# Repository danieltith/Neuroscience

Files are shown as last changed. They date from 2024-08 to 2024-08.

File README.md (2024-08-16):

# Neuroscience

Code and hardware files related to my PhD thesis: "Mapping associations between early life adversity and alcohol use disorder through human epidemiology and rat neurobiology".

[Link to be inserted once publicly available]

References:

Brown LA, Hasan S, Foster RG and Peirson SN. COMPASS: Continuous Open Mouse Phenotyping of Activity and Sleep Status [version 2; peer review: 4 approved]. Wellcome Open Res (2017) 1:2. (https://doi.org/10.12688/wellcomeopenres.9892.2)

Akam T, Lustig A, Rowland JM, Kapanaiah SKT, Esteve-Agraz J, Panniello M, Márquez C, Kohl MM, Kätzel D, Costa RM, Walton ME. Open-source, Python-based, hardware and software for controlling behavioural neuroscience experiments. eLife (2022) 11:e67846. (https://doi.org/10.7554/eLife.67846)

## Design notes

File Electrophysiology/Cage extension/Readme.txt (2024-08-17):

Box extension made of 5mm clear acrylic.
Corners strengthened using 10x10mm acrylic bar.
Contains space to house operant unit or blanking plate during recording. 
N.B if working with female rats would recommend extending height to 30+cm due to climbing.

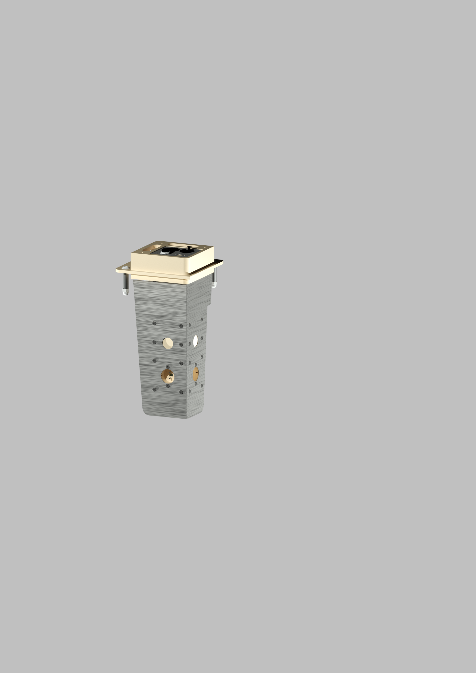
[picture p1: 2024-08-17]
Operant/OperantUnit/Render2.png

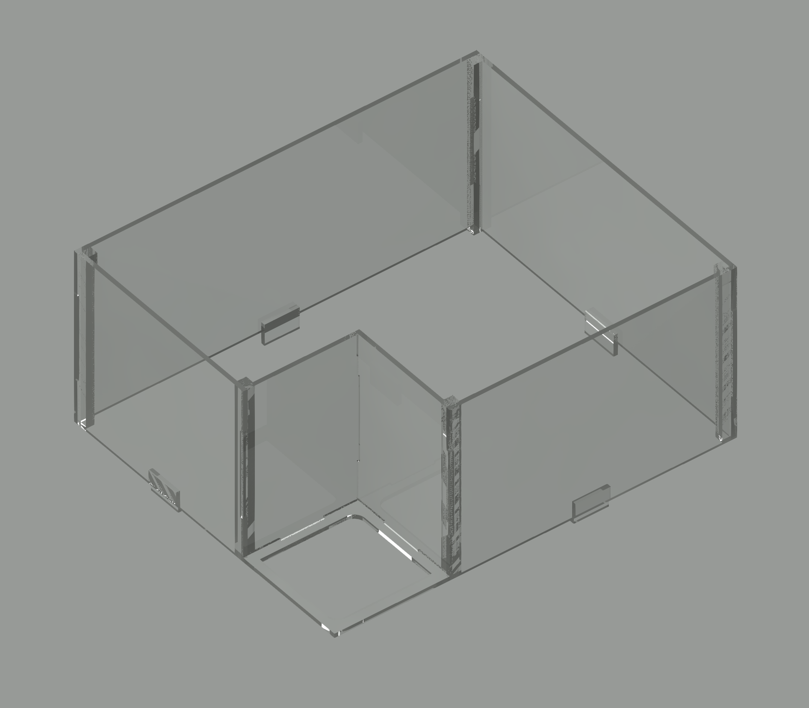
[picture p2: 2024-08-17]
Electrophysiology/Cage extension/Render.png

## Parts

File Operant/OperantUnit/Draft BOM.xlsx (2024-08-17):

Part Name/description | Supplier | Supplier PN | Quantity | Package size | Approx Price per unit | Approx Total
Stainless Steel Pipes/Thin-Walled, 2mm OD, 1mm ID, annealled | Misumi | SPLT2-28 | 2 | 1 | 2.93 € | 5.86 €
TRX Slim Head Screw M3 - 8mm | Misumi | CSXSLH-STN-M3-8 (https://uk.misumi-ec.com/vona2/detail/221005017402/?HissuCode=CSXSLH-STN-M3-8) | 1 | 2000 | 82.44 € | 82.44 €
TRX Slim Head Screw M3 - 16mm | Misumi | CSXSLH-STN-M3-16 (https://uk.misumi-ec.com/vona2/detail/221005017402/?HissuCode=CSXSLH-STN-M3-16) | 1 | 1000 | 54.83 € | 54.83 €
TRX Slim Head Screw M3 - 25mm | Misumi | CSXSLH-STN-M3-25 (https://uk.misumi-ec.com/vona2/detail/221005017402/?HissuCode=CSXSLH-STN-M3-25) | 1 | 500 | 38.14 € | 38.14 €
TRX Slim Head Screw M3 - 30mm | Misumi | CSXSLH-STN-M3-30 (https://uk.misumi-ec.com/vona2/detail/221005017402/?HissuCode=CSXSLH-STN-M3-30) | 1 | 500 | 41.67 € | 41.67 €
10uL fixed volume pump | Lee Company | LPMA1250110L | 2 | 1 | £173.95 | £347.90
Quiet 3 port HDI Solenoid valve | Lee Company | LHQA1231220H | 2 | 1 | £64.11 | £128.22
Stainless steel panels | Cut-Tec | NA | 1 | 1 set
Nosepoke PCBs | Newbury Electronics | NA | 2 | 1
Breakout PCB | Newbury Electronics | NA | 1 | 1
Indicator light PCBs | Newbury Electronics |  | 2 | 1
Pyboard D | Micropython
Molex picoblade cable assemblies | Digikey

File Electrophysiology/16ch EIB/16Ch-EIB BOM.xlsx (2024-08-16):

Description | Quantity | Manufacturer | Manufacturer Part Number | Supplier | Supplier Part Number | Designator | Technology
DF40C(2.0)-70DS-0.4V(51) | 1 | Hirose Connector (https://www.mouser.co.uk/manufacturer/hirose/) | DF40C(2.0)-70DS-0.4V(51) | Mouser | 798-DF40C2070DS04V51 | J1 | SMD
WA-SMSI M1.6 x 2.5mm D3.3mm | 1 | Wurth Elektronik | 97730256330R | Mouser | 710-97730256330R | MP1 | SMD

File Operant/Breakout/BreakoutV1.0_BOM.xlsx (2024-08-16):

Part Number | Designator | Description | Mount | Required Quantitiy | Manufacturer | Manufacturer PN | Supplier | Supplier PN
1 | C1 | Ceramic Capacitor 100V 100nF 0805 | SMD | 1 | KEMET | C0805C104K1RAC7210 | Digikey | 399-C0805C104K1RAC7210CT-ND
2 | C2,C3,C4 | Capacitor 16V 1uF 0603 | SMD | 3 |  |  | Newbury free stock | 0603-1uF-16V
3 | C5,C6,C7,C8 | Capacitor 25V 10uF 1206 | SMD | 4 |  |  | Newbury free stock | 1206-10uf-25V
4 | D1 | Diode Schottky 20V 1A | SMD | 1 | Toshiba | CRS06(TE85L,Q,M) | Digikey | CRS06QMCT-ND
5 | D2 | Diode Schottky 10V 3A | SMD | 1 | Infineon | BAT60AE6327HTSA1 | Digikey | BAT60AE6327HTSA1CT-ND
6 | D3,D4,D5,D6 | Diode TVS 24V 0603 | SMD | 4 | Littelfuse | PGB1010603MR | Digikey | F3801CT-ND
7 | IC1,IC2,IC3 | Driver Array | SMD | 3 | Toshiba | TBD62083AFWG | Digikey | TBD62083AFWGELCT-ND
8 | IC4 | USB TYPE-C PD CTRL, -40 TO 105DEG C | QFN | 1 | STMICROELECTRONICS | STUSB4500QTR | Digikey | 497-18060-1-ND
9 | J1 | USB-C connector | THT | 1 | Amphenol ICC (Commercial Products) | MUSBRM1C130 | Digikey | MUSBRM1C130-ND
10 | J2,J3,J4 | 4 pin through hole connector | THT | 3 | Molex | 530470410 | Digikey | WM1733-ND
11 | J5,J6,J7,J8,J9,J10,J11,J12,J13,J14,J15,J16,J17,J18,J19,J20 | 2 pin through hole connector | THT | 16 | Molex | 530470210 | Digikey | WM1731-ND
12 | J21,J22,J23 | 5 pin through hole connector | THT | 3 | Molex | 530470510 | Digikey | WM1734-ND
13 | Q1 | Power MOSFET | SMD | 1 | STMICROELECTRONICS | STL9P3LLH6 | Digikey | 497-17897-1-ND
14 | R1,R2,R3,R4,R5,R6 | 100 resistor; 0603; 0.1W | SMD | 6 |  |  | Newbury free stock | 0603-100R
15 | R7,R8 | 1k resistor; 0603; 0.1W | SMD | 2 |  |  | Newbury free stock | 0603-1K
16 | R9,R10,R11,R12 | 2.2k resistor; 0603; 0.1W | SMD | 4 |  |  | Newbury free stock | 0603-2K2
17 | R13 | 22k resistor; 0603; 0.1W | SMD | 1 |  |  | Newbury free stock | 0603-22K
18 | R14,R15,R16,R17,R18 | 100k resistor; 0603; 0.1W | SMD | 5 |  |  | Newbury free stock | 0603-100K
19 | S1,S2,S3 | SPST push switch | SMD | 3 | OMRON | B3FS-1012P | Digikey | SW1440CT-ND
20 | U1 | 5V 1A DC DC Converter | THT | 1 | Recom Power | R-78E5.0-1.0 | Digikey | 945-2201-ND
21 | U2 | 12V 1A DC DC Converter | THT | 1 | Recom Power | R-78E12-1.0/X9 | Digikey | 945-R-78E12-1.0/X9-ND
22 | X1,X2 | WBUS40 connector | SMD | 2 | Hirose Electric Co Ltd | DF40HC(4.0)-40DS-0.4V(70) | Digikey | H124604CT-ND

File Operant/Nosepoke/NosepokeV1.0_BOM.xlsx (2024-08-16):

Part Number | Designator | Description | Mount | Quantity | Manufacturer | Manufacturer PN | Supplier | Supplier PN
1 | C1,C2 | 10 uF Capacitor 0603 | SMD | 2 |  |  | Newbury free stock | 0603-10uF-6.3V
2 | C3 | 100nF Capacitor 0603 | SMD | 1 |  |  | Newbury free stock | 0603-100nF-25V
3 | J1,J2 | Right angle header | THT | 2 | SAMTEC | SSW-102-02-T-S-RA | Digikey | SAM11929-ND
4 | J3,J4,J5,J6,J7 | 2 pin connector | THT | 5 | Molex | 530470210 | Digikey | 455-1611-ND
5 | J8 | 5 pin connector | THT | 1 | Molex | 530470510 | Digikey | WM1734-ND
6 | Q1,Q2 | Mosfet | SMD | 2 |  | BSS138 | Farnell | 9845330
7 | R1 | 220R resistor 0603 | SMD | 1 |  |  | Newbury free stock | 0603-220R
8 | R2,R3,R4,R5,R6 | 10k resistor 0603 | SMD | 5 |  |  | Newbury free stock | 0603-10k
9 | R7,R8 | 47k resistor 0603 | SMD | 2 |  |  | Newbury free stock | 0603-47K
10 | U1 | TOF sensor | Leadless | 1 | ST Microelectronics | VL6180XV0NR/1 | Digikey | 497-14702-1-ND
11 | U2 | LP5907 2.8V LDO | SMD | 1 | TEXAS INSTRUMENTS | LP5907MFX-2.8/NOPB | Farnell | 3007717

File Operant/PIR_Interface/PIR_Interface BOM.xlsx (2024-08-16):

Description | Quantity | Manufacturer | Manufacturer Part Number | Supplier | Supplier Part Number | Designator | Technology
Arduino Nano v.3.x (ATmega328) | 1 | Arduino | A000005 | Digikey | 1050-1001-ND | A1 | THT
12 port ethernet connector | 1 | Stewart Connector | SS73100-046F | Digikey | 380-1225-ND | J1 | THT

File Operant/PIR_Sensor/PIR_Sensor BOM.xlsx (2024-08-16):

Description | Quantity | Manufacturer | Manufacturer Part Number | Supplier | Supplier Part Number | Designator | Technology
RJ45 jack | 1 | AMPHENOL | 54601-908WPLF | Digikey | 609-5081-ND | J1 | THT
8 pin header (2.54mm) | 1 | Wurth Electronic | 61300811821 | Digikey | 732-61300811821-ND | J2 | THT
5V PIR sensor (AMN32111) | 1 | Panasonic | AMN32111 | Digikey | 255-2645-ND | U1 | THT
SMD resistor (6K2; 1%; 0.25W; 1206) | 2 | STACKPOLE ELECTRONICS INC (VA) | RMCF1206FT6K20 | Digikey | RMCF1206FT6K20CT-ND | R1, R5, | SMD
SMD resistor (10K; 1%; 0.5W; 1206) | 2 | STACKPOLE ELECTRONICS INC (VA) | RNCP1206FTD10K0 | Digikey | RNCP1206FTD10K0CT-ND | R2, R4 | SMD
Light Dependent Resistor | 1 |  |  |  |  | R3 | THT
Black ABS Potting Box Enclosure with Lid - 39.5x27.5x17.5mm - | 1 | Evatron | RX2006 | Farnell | EN84693 | NA | NA

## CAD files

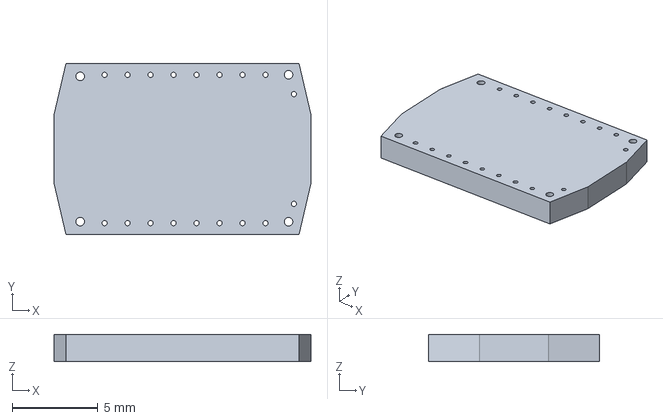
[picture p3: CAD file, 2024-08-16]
Electrophysiology/16ch EIB/KiCAD project/eob-16.step
15.0 x 10.0 x 1.60 mm

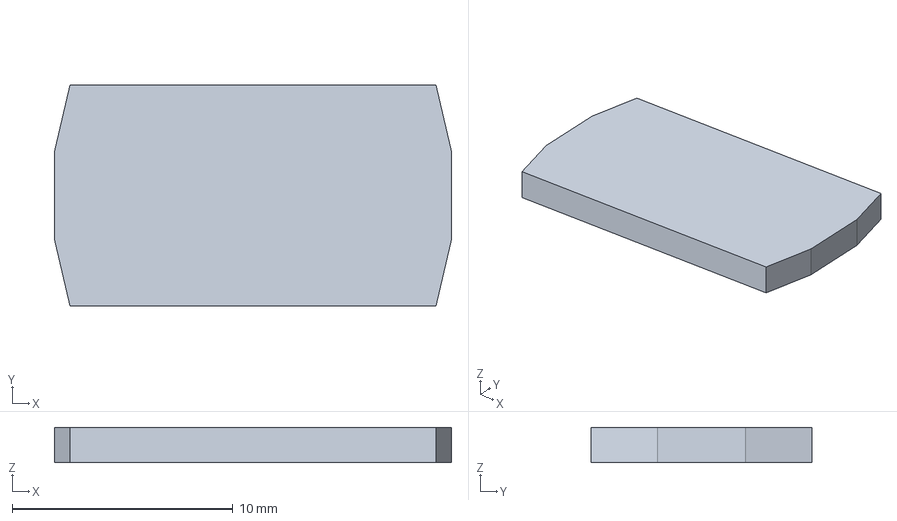
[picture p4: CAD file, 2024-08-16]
Electrophysiology/Head cap for 16ch EIB/KiCAD/12X18_CAP.step
18.0 x 10.0 x 1.60 mm

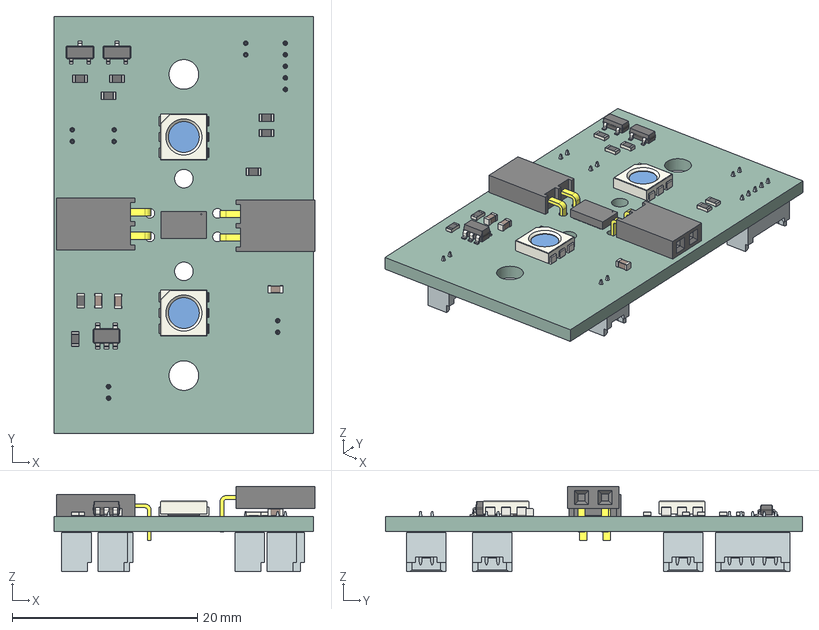
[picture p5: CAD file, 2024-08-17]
Operant/Nosepoke/KiCadFiles/NosepokeV1.0.step
28.1 x 45.0 x 9.21 mm
C_0603_1608Metric x 3
SOT_23 x 2
R_0603_1608Metric x 8
ssw-102-02-t-s-ra x 2
LED_RGB_5050_6 x 2
SOT_23_5
530470210wbm000_01 x 5
530470510wbm000_01
_autosave-NosepokeV1.0_PCB

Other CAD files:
Electrophysiology/Cage extension/FinalCageExtension.dwg

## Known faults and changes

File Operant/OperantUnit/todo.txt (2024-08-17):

1) Update BOM
2) Include laser cutting sheets

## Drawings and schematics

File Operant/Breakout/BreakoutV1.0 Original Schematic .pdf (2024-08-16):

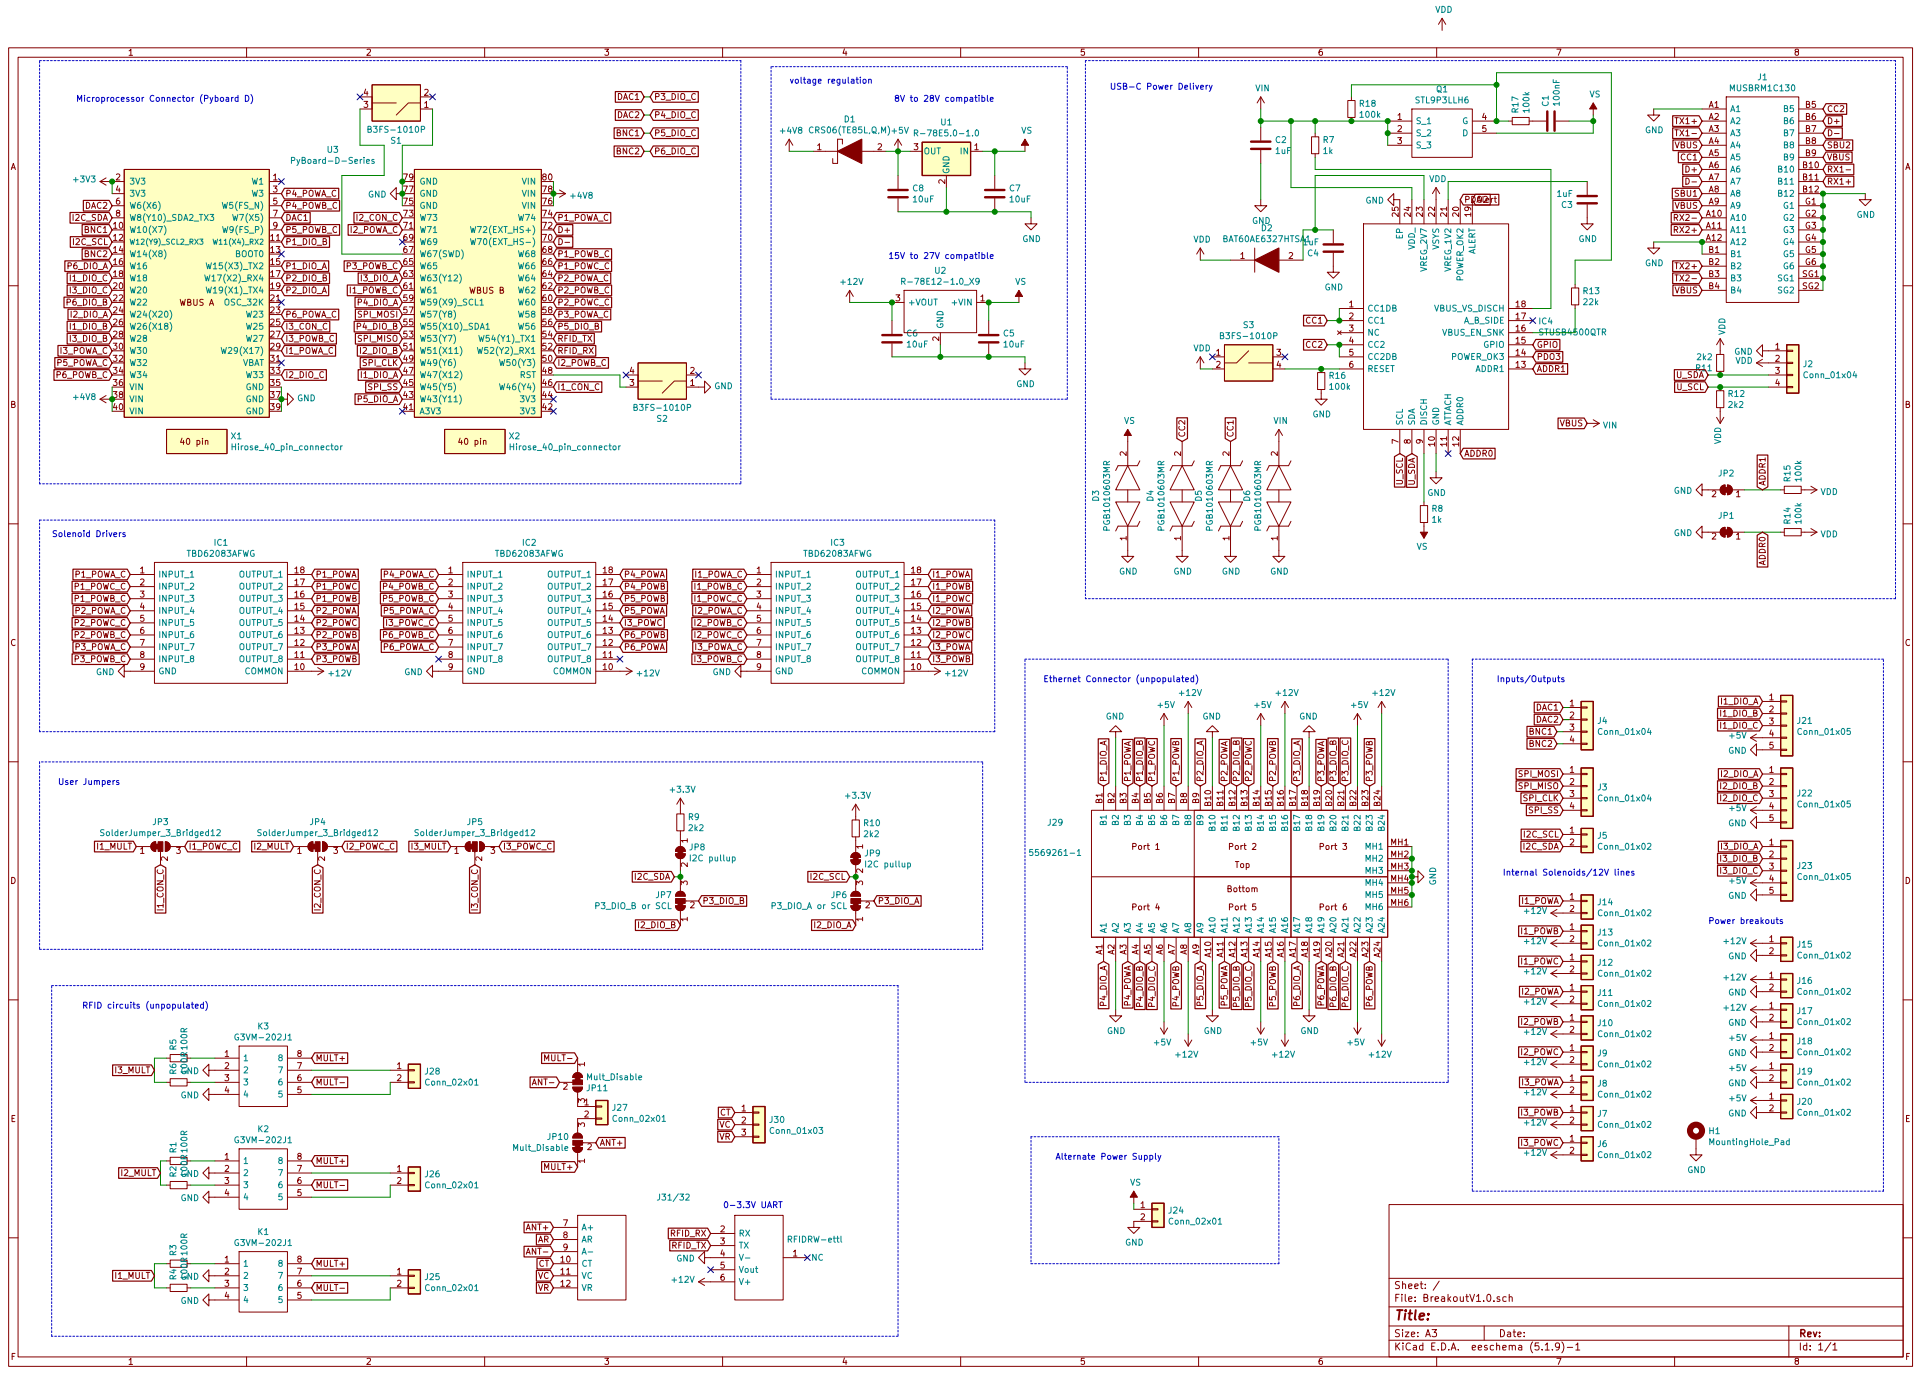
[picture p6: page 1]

Ethernet Connector (unpopulated) Solenoid Drivers

P1_POWA P1_DIO_B P1_POWC P1_POWB | P2_DIO_A P2_POWA P2_DIO_B P2_POWC P2_POWB | I1_POWC P1_DIO_A

Bottom

Id: 1/1 Title: File: BreakoutV1.0.sch Sheet: / GND

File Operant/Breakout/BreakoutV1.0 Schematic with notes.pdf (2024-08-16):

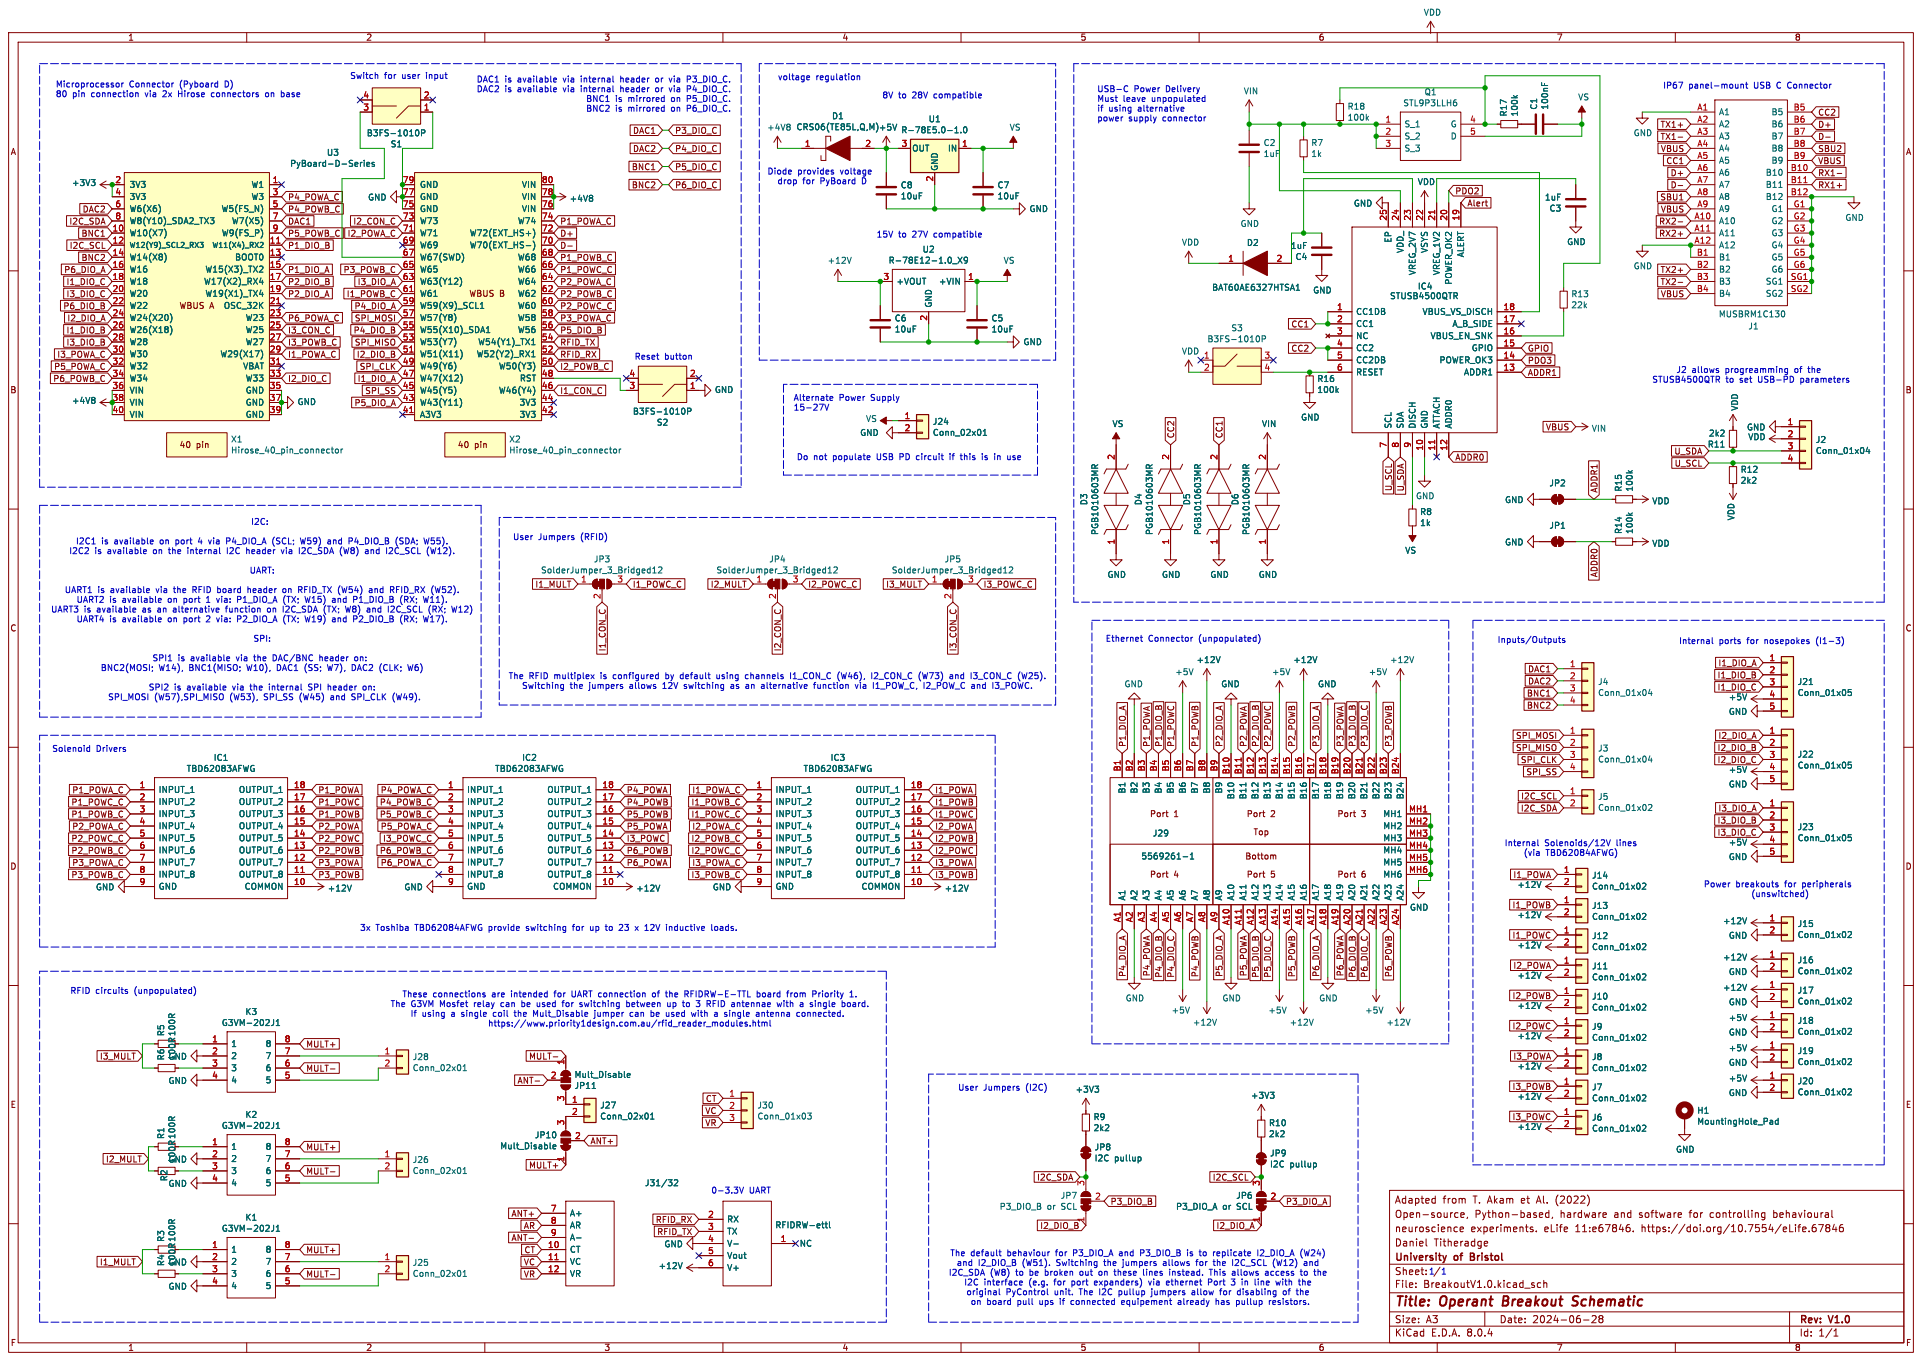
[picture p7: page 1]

15V to 27V compatible Switch for user input

USB-C Power Delivery Must leave unpopulated

Bottom

3 +12V GND GND GND GND

I2C_SDA (W8) to be broken out on these lines instead. This allows access to the

Id: 1/1 Title: Operant Breakout Schematic

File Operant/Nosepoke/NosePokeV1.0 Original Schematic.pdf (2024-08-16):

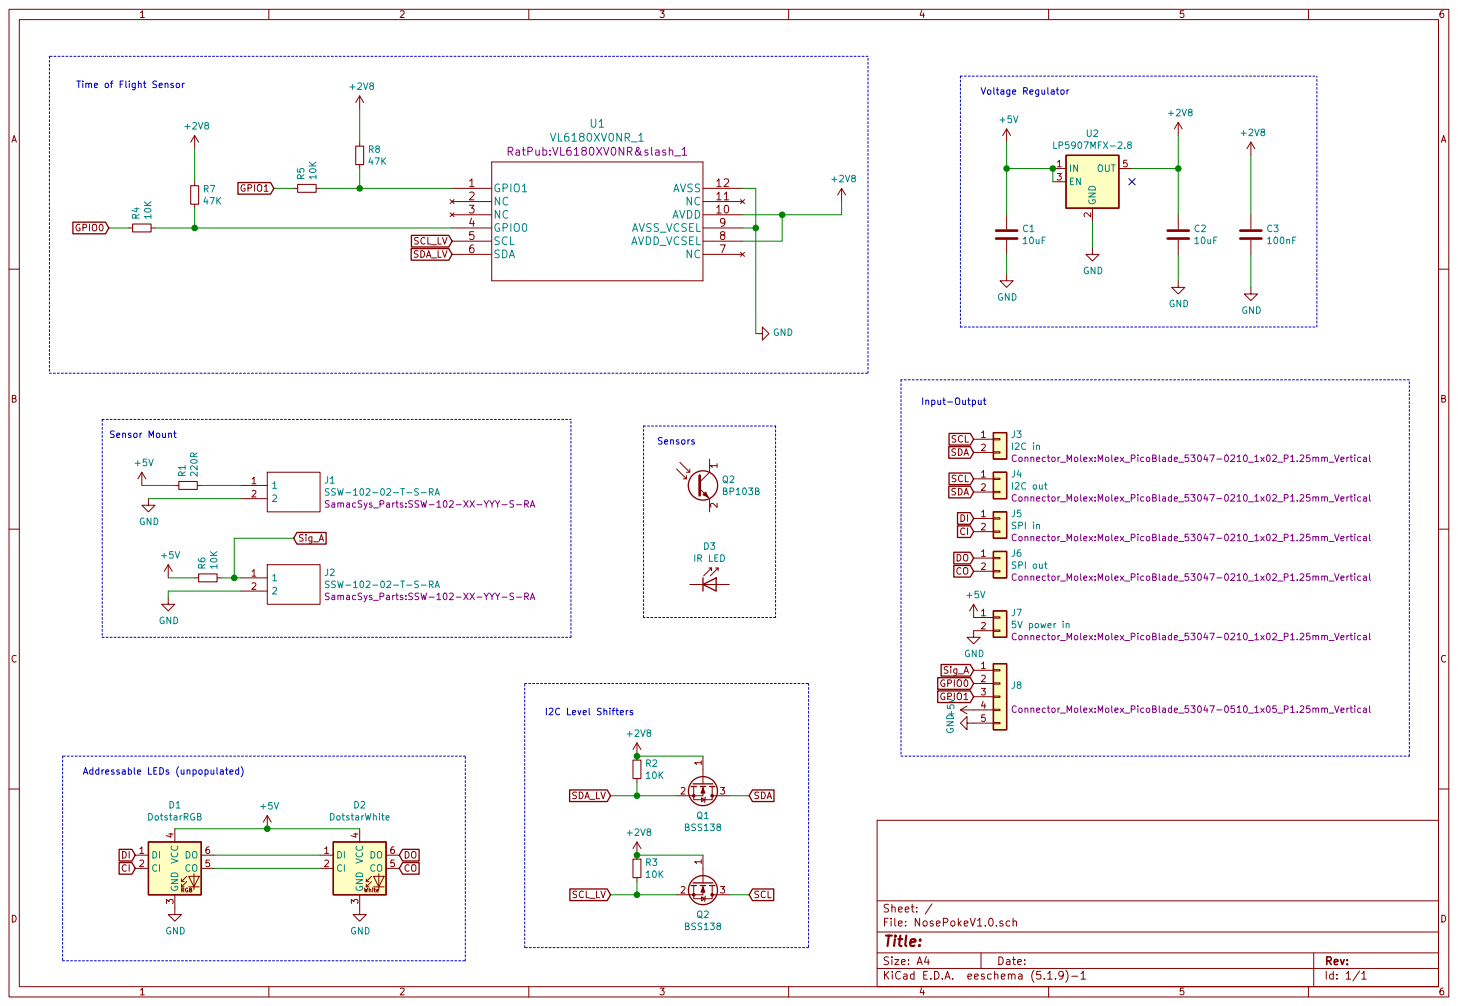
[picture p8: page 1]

Voltage Regulator Time of Flight Sensor

Input-Output Sensor Mount

SamacSys_Parts:SSW-102-XX-YYY-S-RA R610K

SamacSys_Parts:SSW-102-XX-YYY-S-RA

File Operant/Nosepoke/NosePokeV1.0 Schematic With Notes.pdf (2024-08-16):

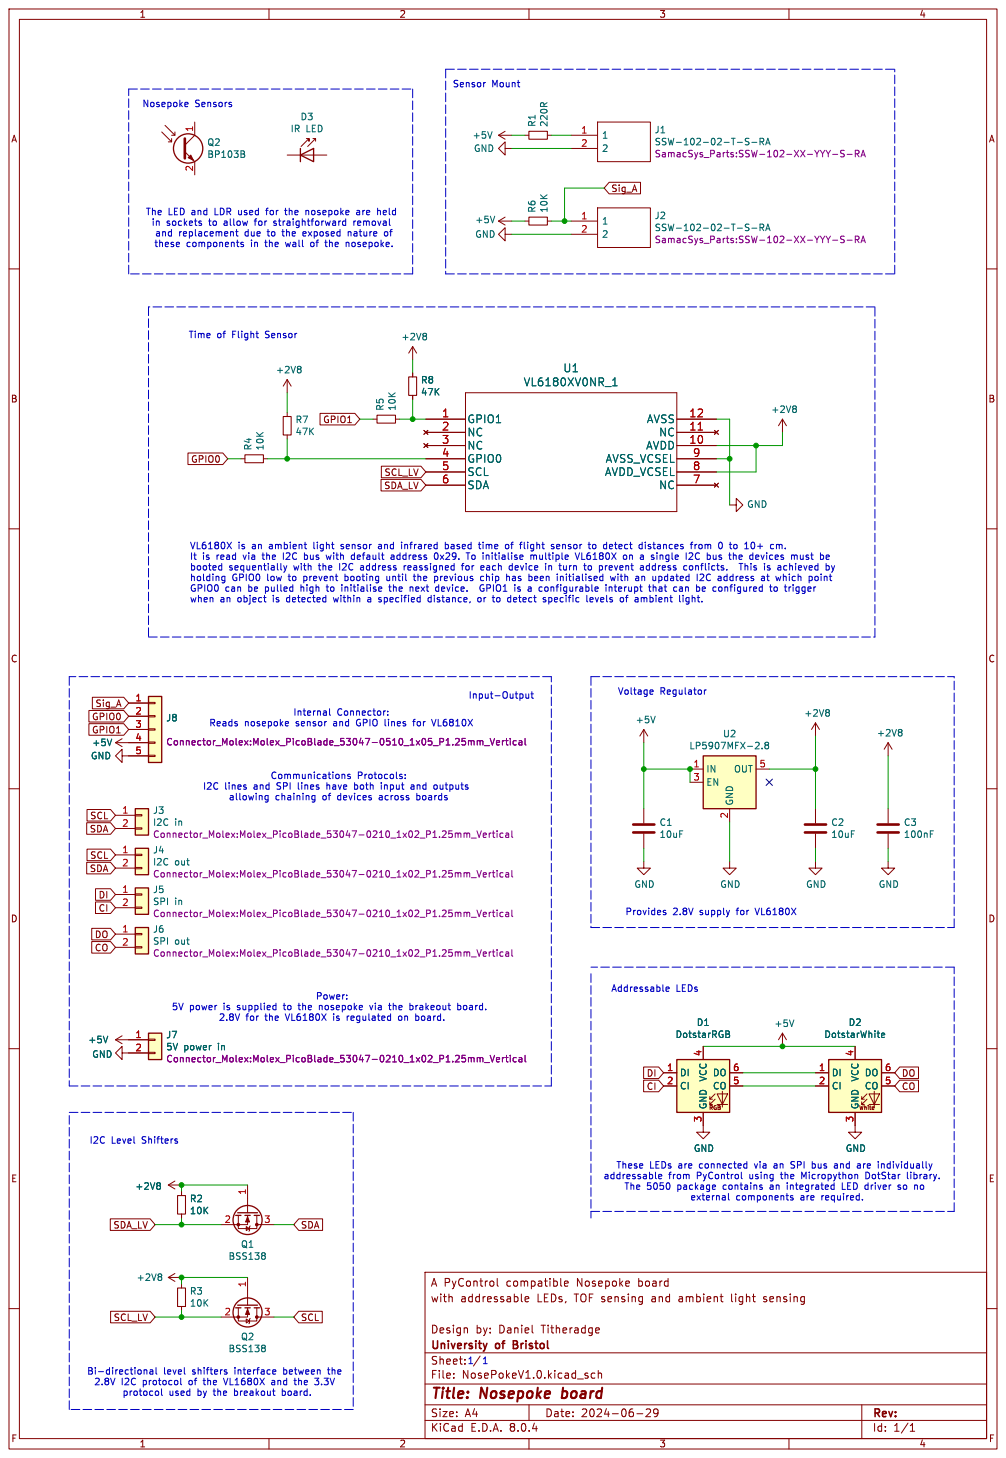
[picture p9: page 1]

Nosepoke Sensors The LED and LDR used for the nosepoke are held

SamacSys_Parts:SSW-102-XX-YYY-S-RA

4 CO 5 DO 6 D1 DotstarRGB GND

Id: 1/1 Title: Nosepoke board

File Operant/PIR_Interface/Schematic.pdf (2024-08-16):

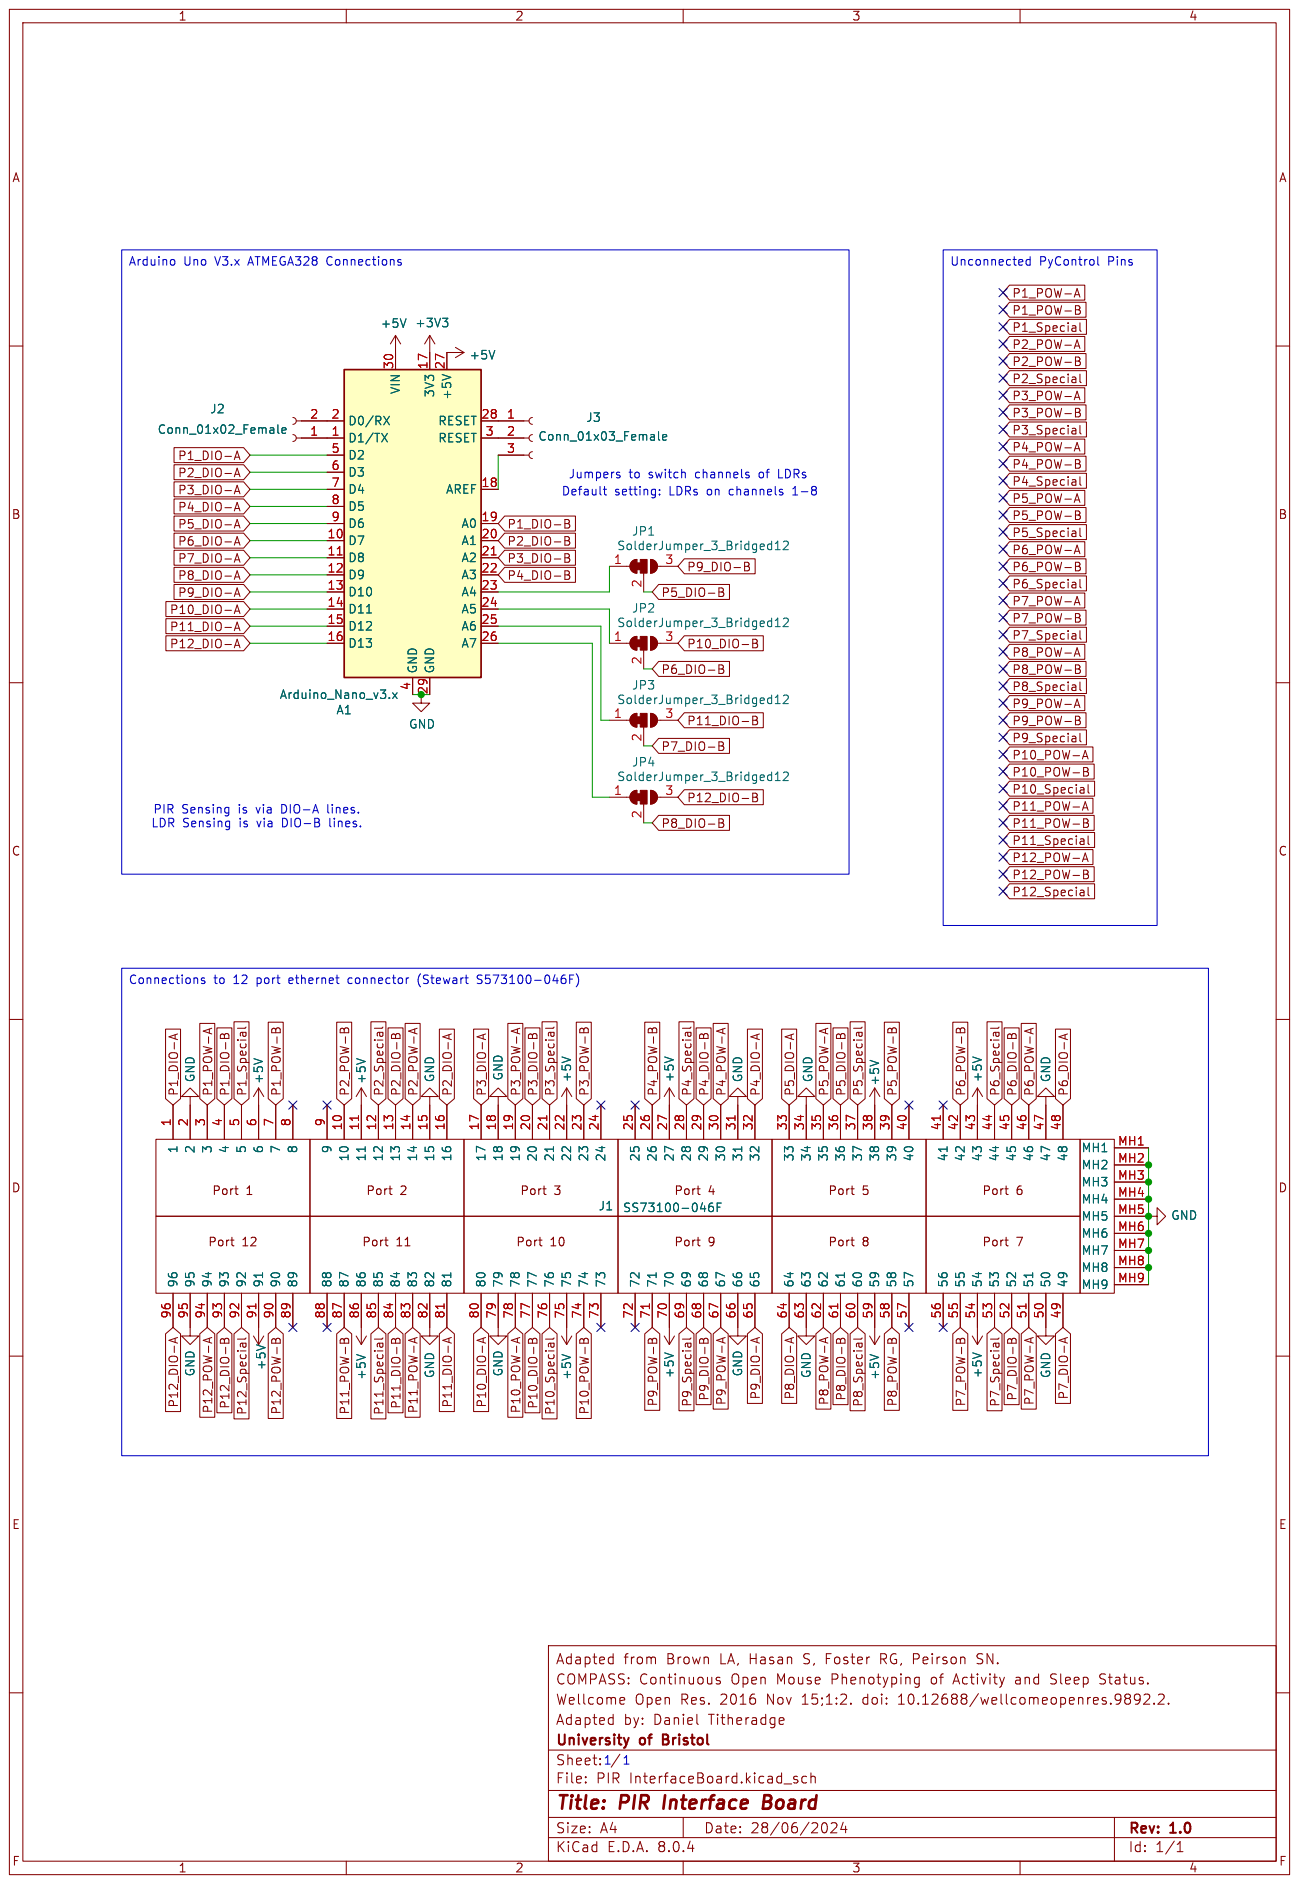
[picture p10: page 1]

Id: 1/1 Title: PIR Interface Board

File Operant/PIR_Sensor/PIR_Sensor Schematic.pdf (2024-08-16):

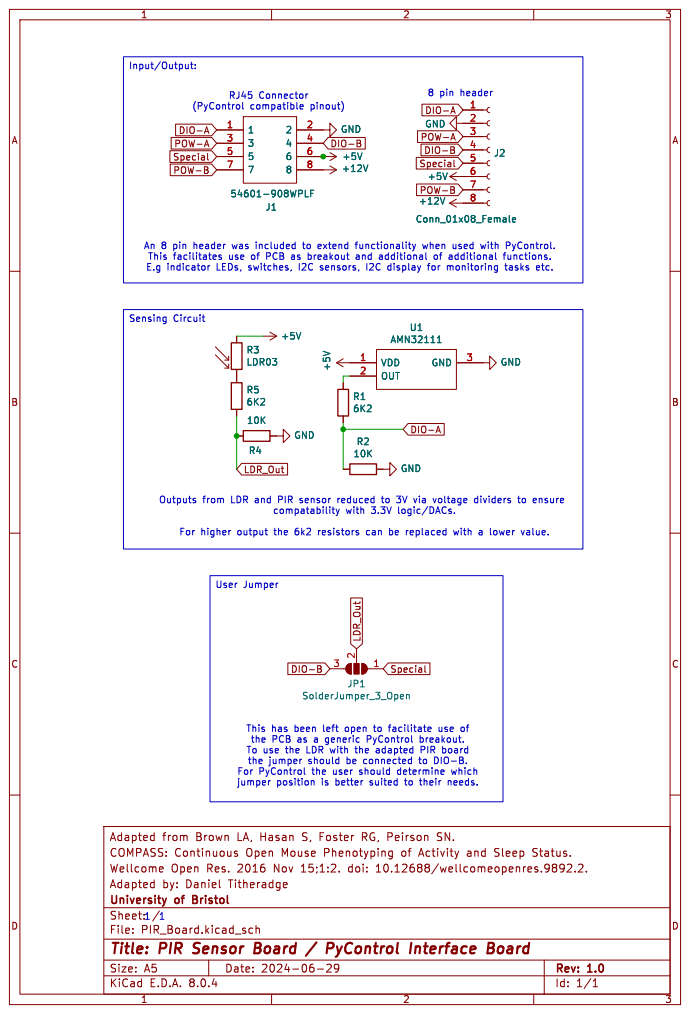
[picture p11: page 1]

Outputs from LDR and PIR sensor reduced to 3V via voltage dividers to ensure

Id: 1/1 Title: PIR Sensor Board / PyControl Interface Board

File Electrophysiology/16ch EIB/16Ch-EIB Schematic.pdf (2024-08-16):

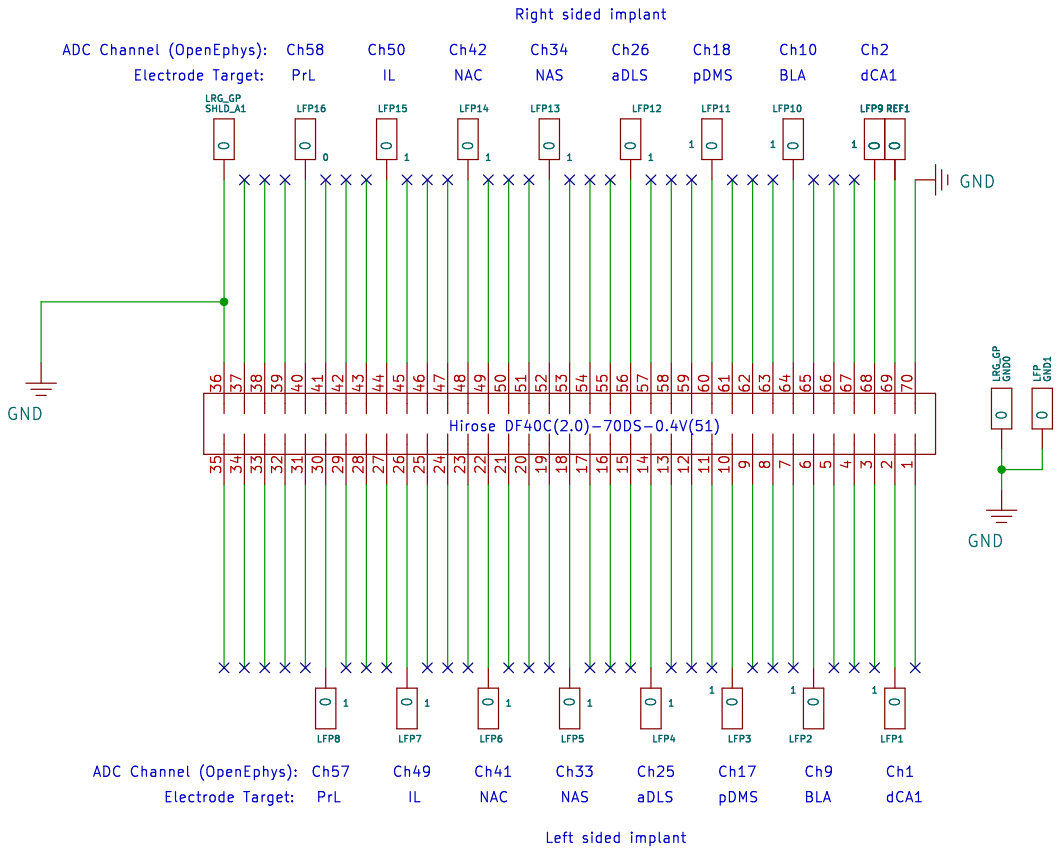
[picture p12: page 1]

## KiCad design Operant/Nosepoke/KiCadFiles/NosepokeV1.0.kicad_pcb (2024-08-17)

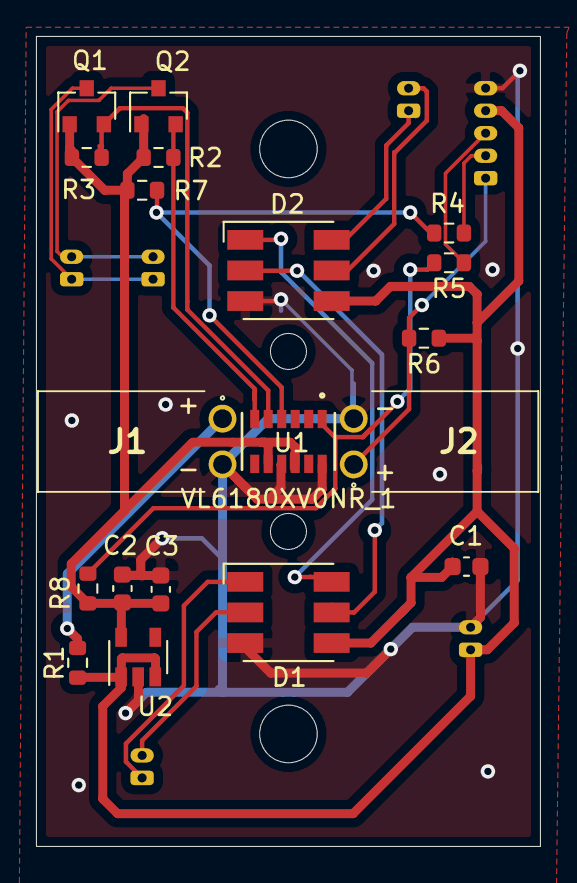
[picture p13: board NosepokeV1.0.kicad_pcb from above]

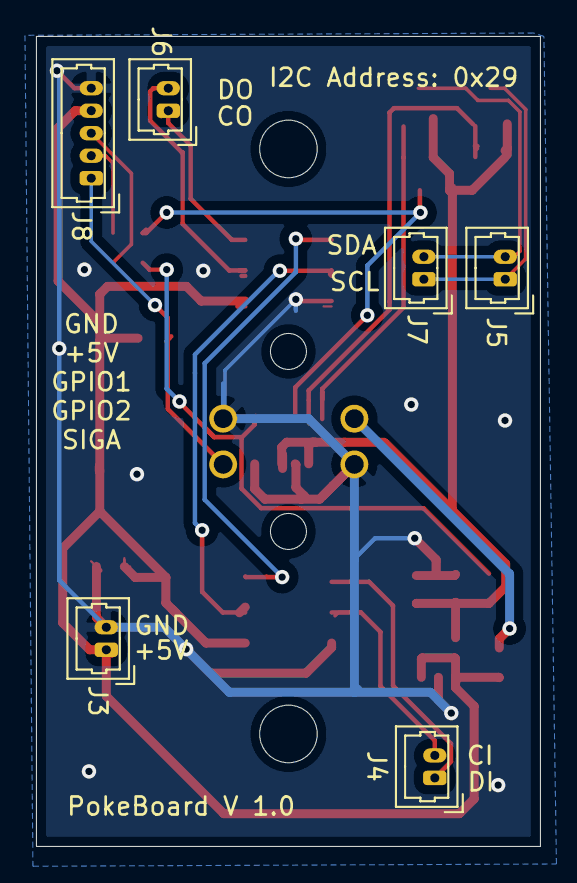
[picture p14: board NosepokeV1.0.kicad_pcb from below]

Board: 2 copper layers, 28.0 x 45.0 mm, 27 parts (6 on the bottom side), 19 nets.

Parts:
C1, C2: 10uF; C_0603_1608Metric
C3: 100nF; C_0603_1608Metric
D1: DotstarRGB; LED_RGB_5050-6
D2: DotstarWhite; LED_RGB_5050-6
J1, J2: SSW-102-02-T-S-RA; SSW-102-XX-YYY-S-RA
J3: 5V power in; Molex_PicoBlade_53047-0210_1x02_P1.25mm_Vertical
J4: SPI in; Molex_PicoBlade_53047-0210_1x02_P1.25mm_Vertical
J5: I2C in; Molex_PicoBlade_53047-0210_1x02_P1.25mm_Vertical
J6: SPI out; Molex_PicoBlade_53047-0210_1x02_P1.25mm_Vertical
J7: I2C out; Molex_PicoBlade_53047-0210_1x02_P1.25mm_Vertical
J8: Conn_01x03; Molex_PicoBlade_53047-0510_1x05_P1.25mm_Vertical
Mount1, Mount2: MountingHole_3.2mm_M3
Q1, Q2: BSS138; SOT-23
R1: 220R; R_0603_1608Metric
R2, R3, R4, R5, R6: 10K; R_0603_1608Metric
R7, R8: 47K; R_0603_1608Metric
U1: VL6180XV0NR_1; VL6180XV0NR&slash_1
U2: LP5907MFX-2.8; SOT-23-5

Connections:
+2V8: C2.1, C3.1, Q1.1, Q2.1, R2.1, R3.1, R7.1, R8.1, U1.8, U1.10, U2.5
+5V: C1.1, D1.4, D2.4, J3.1, J8.4, R1.1, R6.1, U2.1, U2.3
CI: D1.2, J4.2
CO: D2.5, J6.2
DI: D1.1, J4.1
DO: D2.6, J6.1
GND: C1.2, C2.2, C3.2, D1.3, D2.3, J1.2, J2.2, J3.2, J8.5, U1.9, U1.12, U2.2
GPIO0: J8.2, R4.1
GPIO1: J8.3, R5.1
unnamed: D1.5, D2.2
unnamed: D1.6, D2.1
unnamed: J1.1, R1.2
unnamed: R4.2, R7.2, U1.4
unnamed: R5.2, R8.2, U1.1
SCL: J5.1, J7.1, Q1.3
SCL_LV: Q1.2, R3.2, U1.5
SDA: J5.2, J7.2, Q2.3
SDA_LV: Q2.2, R2.2, U1.6
Sig_A: J2.1, J8.1, R6.2

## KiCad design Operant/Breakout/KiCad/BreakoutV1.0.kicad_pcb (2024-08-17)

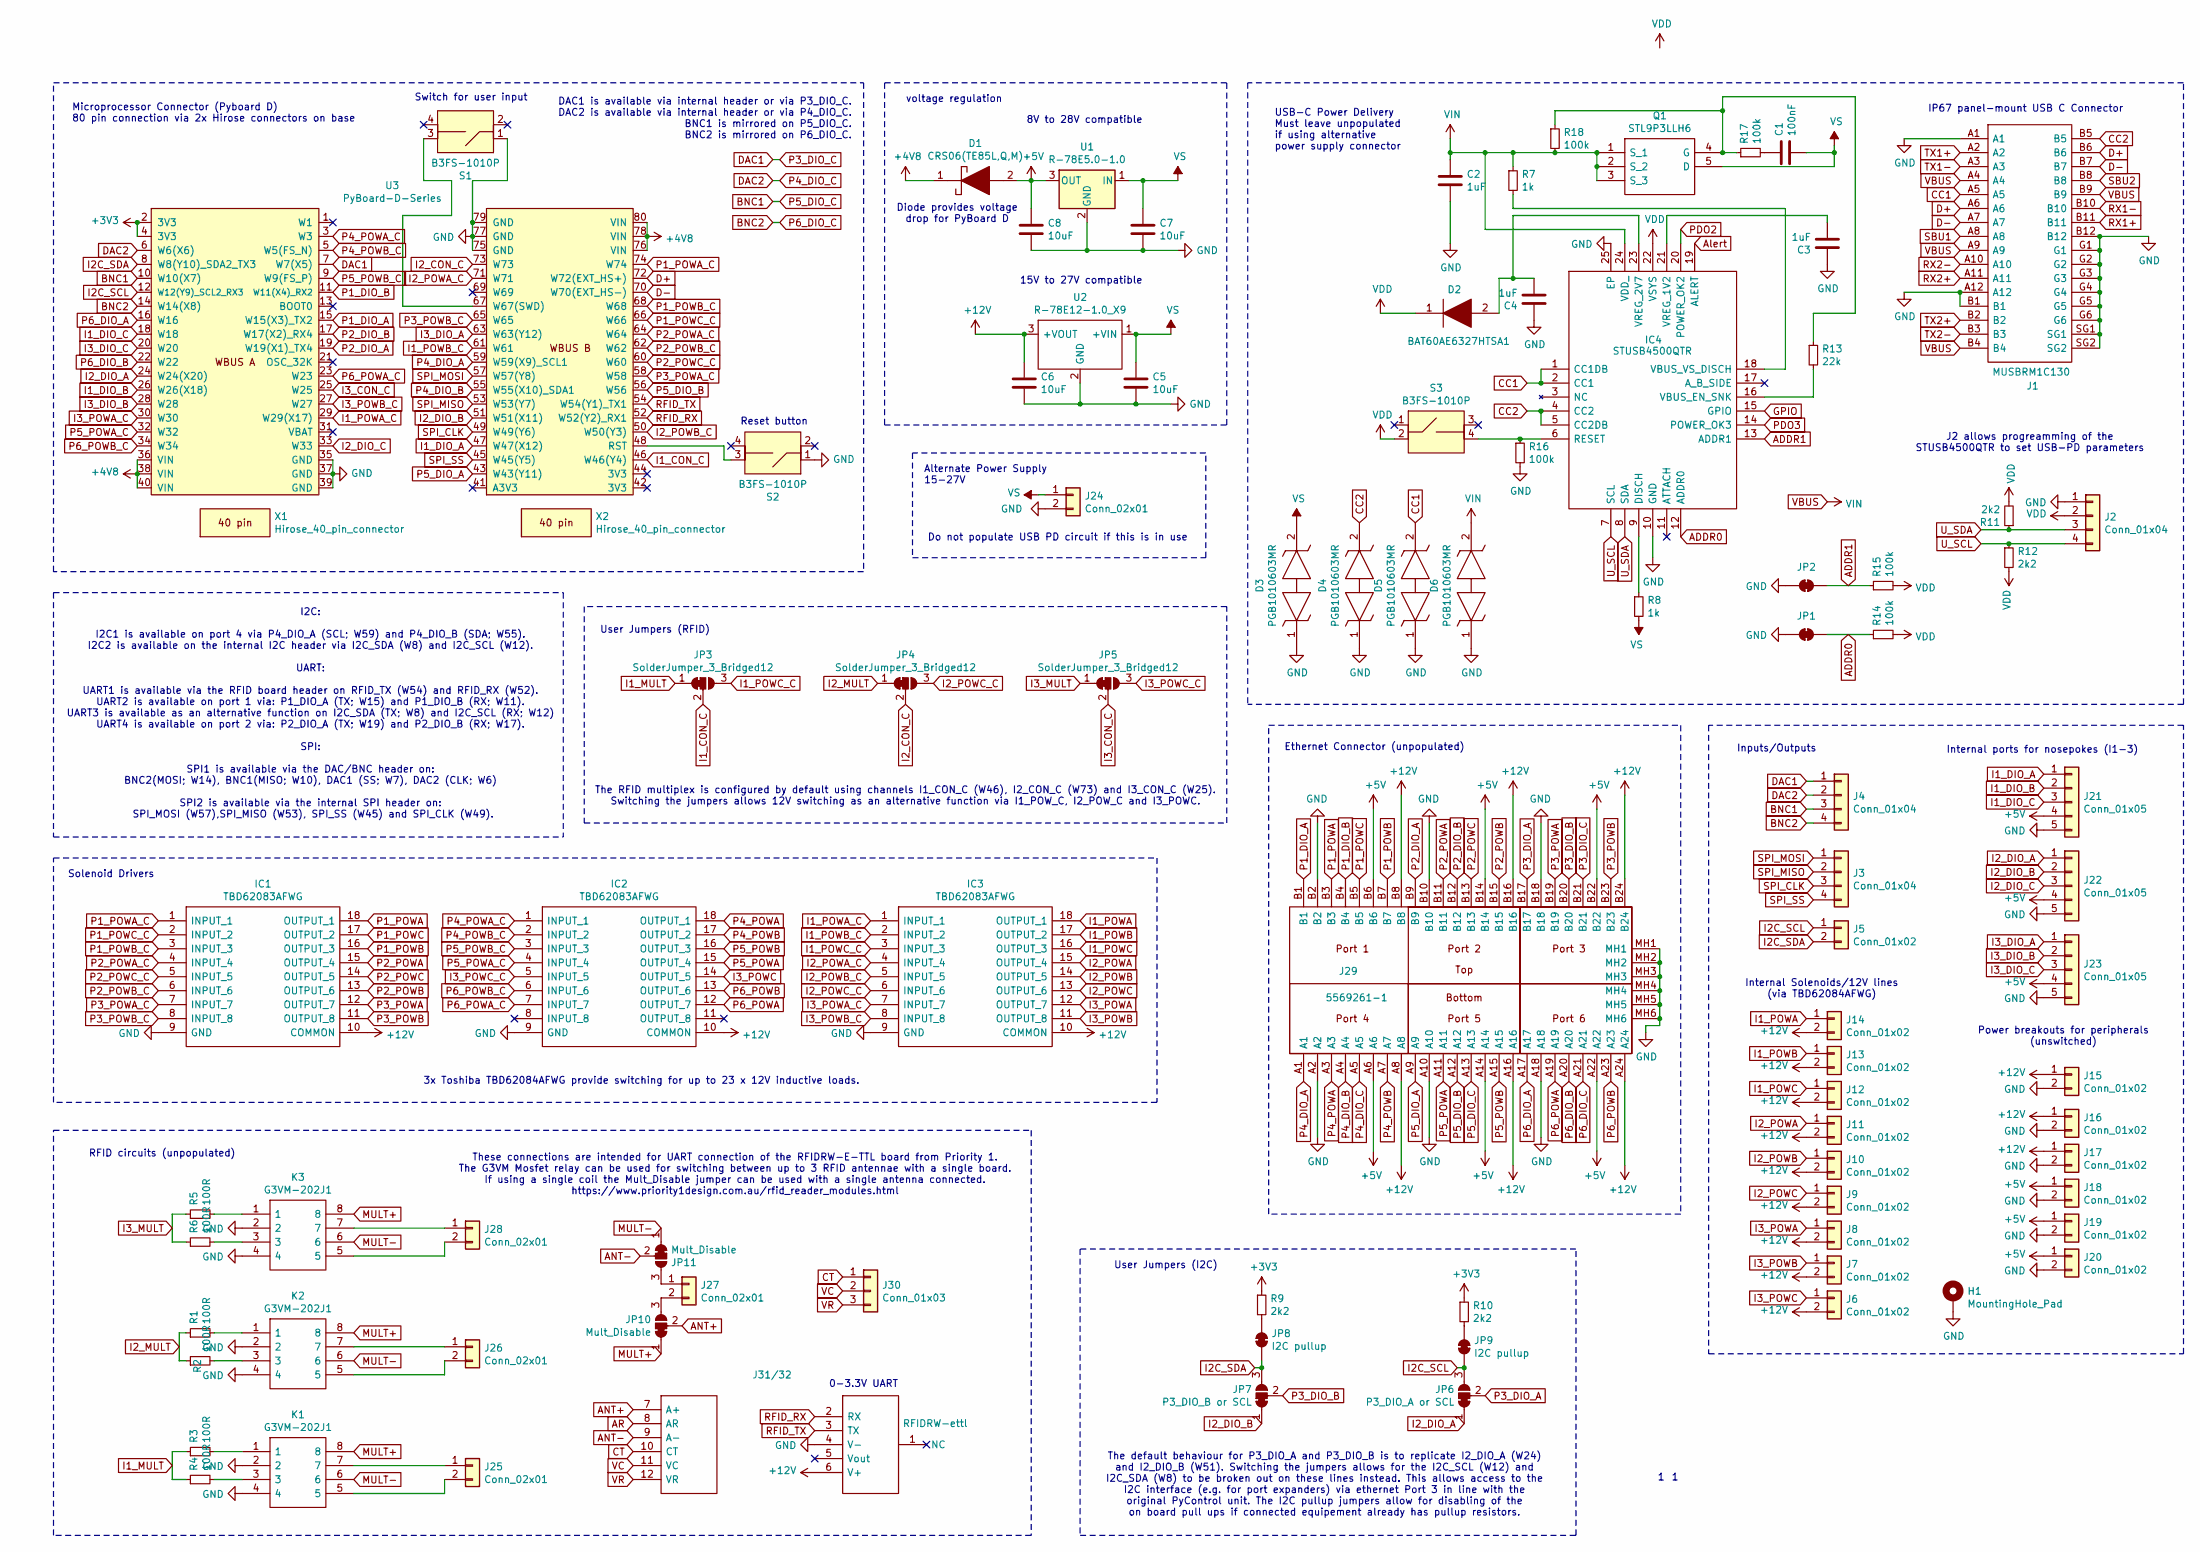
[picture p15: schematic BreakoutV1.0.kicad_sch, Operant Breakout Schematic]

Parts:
C1: 100nF; C_0805_2012Metric
C2, C3, C4: 1uF; C_0603_1608Metric
C5, C6, C7, C8: 10uF; C_1206_3216Metric
D1: CRS06(TE85L,Q,M); S-FLAT-2; Mouser Part Number 863-MBR120VLSFT3G
D2: BAT60AE6327HTSA1; SOD2513X110N; Mouser Part Number 726-BAT60AE6327HTSA1
D3, D4, D5, D6: PGB1010603MR; Mouser Part Number 576-PGB1010603MR
H1: MountingHole_Pad; SolderWirePad_single_1-2mmDrill
IC1, IC2, IC3: TBD62083AFWG; SOIC127P1030X245-18N; Mouser Part Number 757-TBD62083APG
IC4: STUSB4500QTR; QFN50P400X400X100-25N-D; Mouser Part Number 511-STUSB4500QTR
J1: MUSBRM1C130; Mouser Part Number 523-MUSBRM1C130
J2, J3, J4: Conn_01x04; Molex_PicoBlade_53047-0410_1x04_P1.25mm_Vertical
J5, J6, J7, J8, J9, J10, J11, J12, J13, J14, J15, J16, J17, J18, J19, J20: Conn_01x02; Molex_PicoBlade_53047-0210_1x02_P1.25mm_Vertical
J21, J22, J23: Conn_01x05; Molex_PicoBlade_53047-0510_1x05_P1.25mm_Vertical
J24, J25, J26, J27, J28: Conn_02x01; JST_EH_B2B-EH-A_1x02_P2.50mm_Vertical
J29: 5569261-1; 55692611; Mouser Part Number 571-5569261-1
J30: Conn_01x03; SolderWirePad_3x_0-8mmDrill2
J31/32: RFIDRW-ettl; Manufacturer_Part_Number RFIDRW-e-ttl
JP1, JP2: SolderJumper_2_Bridged; SolderJumper-2_P1.3mm_Bridged_RoundedPad1.0x1.5mm
JP3, JP4, JP5: SolderJumper_3_Bridged12; SolderJumper-3_P1.3mm_Bridged12_RoundedPad1.0x1.5mm_NumberL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
JP6: P3_DIO_A or SCL; SolderJumper-3_P1.3mm_Bridged12_RoundedPad1.0x1.5mm_NumberL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
JP7: P3_DIO_B or SCL; SolderJumper-3_P1.3mm_Bridged12_RoundedPad1.0x1.5mm_NumberL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
JP8, JP9: I2C pullup; SolderJumper-2_P1.3mm_Bridged_RoundedPad1.0x1.5mm
JP10, JP11: Mult_Disable; SolderJumper-3_P1.3mm_Bridged12_RoundedPad1.0x1.5mm_NumberL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
K1, K2, K3: G3VM-202J1; SOP254P700X210-8N; Mouser Part Number 653-G3VM-202J1
Q1: STL9P3LLH6; STL20N6F7; Mouser Part Number 511-STL9P3LLH6
R1, R2, R3, R4, R5, R6: 100R; R_0603_1608Metric
R7, R8: 1k; R_0603_1608Metric
R9, R10, R11, R12: 2k2; R_0603_1608Metric
R13: 22k; R_0603_1608Metric
R14, R15, R16, R17, R18: 100k; R_0603_1608Metric
S1, S2, S3: B3FS-1010P; 6mm_tactile_smd
U1: R-78E5.0-1.0; Converter_DCDC_RECOM_R-78E-0.5_THT
U2: R-78E12-1.0_X9; Converter_DCDC_RECOM_R-78E-0.5_THT; Mouser Part Number 919-R-78E12-1.0/X9
U3: PyBoard-D-Series; PyBoard_D-Series
X1, X2: Hirose_40_pin_connector; Hirose_40_pin

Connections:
+3V3: R9.1, R10.1, U3.2 (3V3), U3.4 (3V3)
+4V8: D1.1, U3.36 (VIN), U3.38 (VIN), U3.40 (VIN), U3.76 (VIN), U3.78 (VIN), U3.80 (VIN)
+5V: C8.1, D1.2, J18.1, J19.1, J20.1, J21.4, J22.4, J23.4, J29.A6, J29.A14, J29.A22, J29.B6, J29.B14, J29.B22, U1.3 (OUT)
+12V: C6.1, IC1.10 (COMMON), IC2.10 (COMMON), IC3.10 (COMMON), J6.2, J7.2, J8.2, J9.2, J10.2, J11.2, J12.2, J13.2, J14.2, J15.1, J16.1, J17.1, J29.A8, J29.A16, J29.A24, J29.B8, J29.B16, J29.B24, J31/32.6 (V+), U2.3 (+VOUT)
ADDR0: IC4.12 (ADDR0), JP1.1 (A), R14.1
ADDR1: IC4.13 (ADDR1), JP2.1 (A), R15.1
ANT+: J31/32.7 (A+), JP10.2 (C)
ANT-: J31/32.9 (A-), JP11.2 (C)
AR: J31/32.8 (AR)
Alert: IC4.19 (ALERT)
BNC1: J4.3, J29.A13, U3.10 (W10(X7))
BNC2: J4.4, J29.A21, U3.14 (W14(X8))
CC1: D5.2, IC4.1 (CC1DB), IC4.2 (CC1), J1.A5
CC2: D4.2, IC4.4 (CC2), IC4.5 (CC2DB), J1.B5
CT: J30.1, J31/32.10 (CT)
D+: J1.A6, J1.B6, U3.72 (W72(EXT_HS+))
D-: J1.A7, J1.B7, U3.70 (W70(EXT_HS-))
DAC1: J4.1, J29.B21, U3.7 (W7(X5))
DAC2: J4.2, J29.A5, U3.6 (W6(X6))
GND: C2.2, C3.1, C4.1, C5.2, C6.2, C7.2, C8.2, D3.1, D4.1, D5.1, D6.1, H1.1, IC1.9 (GND), IC2.9 (GND), IC3.9 (GND), IC4.10 (GND), IC4.25 (EP), J1.A1, J1.A12, J1.B1, J1.B12, J1.G1, J1.G2, J1.G3, J1.G4, J1.G5, J1.G6, J1.SG1, J1.SG2, J2.1, J15.2, J16.2, J17.2, J18.2, J19.2, J20.2, J21.5, J22.5, J23.5, J24.2, J29.A2, J29.A10, J29.A18, J29.B2, J29.B10, J29.B18, J29.MH1, J29.MH2, J29.MH3, J29.MH4, J29.MH5, J29.MH6, J31/32.4 (V-), JP1.2 (B), JP2.2 (B), K1.2, K1.4, K2.2, K2.4, K3.2, K3.4, R16.2, S1.1 (in1), S2.1 (in1), U1.2 (GND), U2.2 (GND), U3.35 (GND), U3.37 (GND), U3.39 (GND), U3.75 (GND), U3.77 (GND), U3.79 (GND)
GPIO: IC4.15 (GPIO)
I1_CON_C: JP3.2 (C), U3.46 (W46(Y4))
I1_DIO_A: J21.1, U3.47 (W47(X12))
I1_DIO_B: J21.2, U3.26 (W26(X18))
I1_DIO_C: J21.3, U3.18 (W18)
I1_MULT: JP3.1 (A), R3.1, R4.1
I1_POWA: IC3.18 (OUTPUT_1), J14.1
I1_POWA_C: IC3.1 (INPUT_1), U3.29 (W29(X17))
I1_POWB: IC3.17 (OUTPUT_2), J13.1
I1_POWB_C: IC3.2 (INPUT_2), U3.61 (W61)
I1_POWC: IC3.16 (OUTPUT_3), J12.1
I1_POWC_C: IC3.3 (INPUT_3), JP3.3 (B)
I2C_SCL: J5.1, JP6.3 (B), JP9.2 (B), U3.12 (W12(Y9)_SCL2_RX3)
I2C_SDA: J5.2, JP7.3 (B), JP8.2 (B), U3.8 (W8(Y10)_SDA2_TX3)
I2_CON_C: JP4.2 (C), U3.73 (W73)
I2_DIO_A: J22.1, JP6.1 (A), U3.24 (W24(X20))
I2_DIO_B: J22.2, JP7.1 (A), U3.51 (W51(X11))
I2_DIO_C: J22.3, U3.33 (W33)
I2_MULT: JP4.1 (A), R1.1, R2.1
I2_POWA: IC3.15 (OUTPUT_4), J11.1
I2_POWA_C: IC3.4 (INPUT_4), U3.71 (W71)
I2_POWB: IC3.14 (OUTPUT_5), J10.1
I2_POWB_C: IC3.5 (INPUT_5), U3.50 (W50(Y3))
I2_POWC: IC3.13 (OUTPUT_6), J9.1
I2_POWC_C: IC3.6 (INPUT_6), JP4.3 (B)
I3_CON_C: JP5.2 (C), U3.25 (W25)
I3_DIO_A: J23.1, U3.63 (W63(Y12))
I3_DIO_B: J23.2, U3.28 (W28)
I3_DIO_C: J23.3, U3.20 (W20)
I3_MULT: JP5.1 (A), R5.1, R6.1
I3_POWA: IC3.12 (OUTPUT_7), J8.1
I3_POWA_C: IC3.7 (INPUT_7), U3.30 (W30)
I3_POWB: IC3.11 (OUTPUT_8), J7.1
I3_POWB_C: IC3.8 (INPUT_8), U3.27 (W27)
I3_POWC: IC2.14 (OUTPUT_5), J6.1
I3_POWC_C: IC2.5 (INPUT_5), JP5.3 (B)
MULT+: JP10.1 (A), K1.8, K2.8, K3.8
MULT-: JP11.1 (A), K1.6, K2.6, K3.6
unnamed: C1.1, R17.2
unnamed: C3.2, IC4.21 (VREG_1V2)
unnamed: C4.2, D2.2, IC4.23 (VREG_2V7)
unnamed: IC4.6 (RESET), R16.1, S3.4 (out2)
unnamed: IC4.9 (DISCH), R8.1
unnamed: IC4.16 (VBUS_EN_SNK), R13.2
unnamed: IC4.18 (VBUS_VS_DISCH), R7.2
unnamed: J25.1, K1.7
unnamed: J25.2, K1.5
unnamed: J26.1, K2.7
unnamed: J26.2, K2.5
unnamed: J27.1, JP11.3 (B)
unnamed: J27.2, JP10.3 (B)
unnamed: J28.1, K3.7
unnamed: J28.2, K3.5
unnamed: JP8.1 (A), R9.2
unnamed: JP9.1 (A), R10.2
unnamed: K1.1, R3.2
unnamed: K1.3, R4.2
unnamed: K2.1, R1.2
unnamed: K2.3, R2.2
unnamed: K3.1, R5.2
unnamed: K3.3, R6.2
unnamed: Q1.4 (G), R13.1, R17.1, R18.1
unnamed: S1.3 (out1), U3.67 (W67(SWD))
unnamed: S2.3 (out1), U3.48 (RST)
P1_DIO_A: J29.B1, U3.15 (W15(X3)_TX2)
P1_DIO_B: J29.B4, U3.11 (W11(X4)_RX2)
P1_POWA: IC1.18 (OUTPUT_1), J29.B3
P1_POWA_C: IC1.1 (INPUT_1), U3.74 (W74)
P1_POWB: IC1.16 (OUTPUT_3), J29.B7
P1_POWB_C: IC1.3 (INPUT_3), U3.68 (W68)
P1_POWC: IC1.17 (OUTPUT_2), J29.B5
P1_POWC_C: IC1.2 (INPUT_2), U3.66 (W66)
P2_DIO_A: J29.B9, U3.19 (W19(X1)_TX4)
P2_DIO_B: J29.B12, U3.17 (W17(X2)_RX4)
P2_POWA: IC1.15 (OUTPUT_4), J29.B11
P2_POWA_C: IC1.4 (INPUT_4), U3.64 (W64)
P2_POWB: IC1.13 (OUTPUT_6), J29.B15
P2_POWB_C: IC1.6 (INPUT_6), U3.62 (W62)
P2_POWC: IC1.14 (OUTPUT_5), J29.B13
P2_POWC_C: IC1.5 (INPUT_5), U3.60 (W60)
P3_DIO_A: J29.B17, JP6.2 (C)
P3_DIO_B: J29.B20, JP7.2 (C)
P3_POWA: IC1.12 (OUTPUT_7), J29.B19
P3_POWA_C: IC1.7 (INPUT_7), U3.58 (W58)
P3_POWB: IC1.11 (OUTPUT_8), J29.B23
P3_POWB_C: IC1.8 (INPUT_8), U3.65 (W65)
P4_DIO_A: J29.A1, U3.59 (W59(X9)_SCL1)
P4_DIO_B: J29.A4, U3.55 (W55(X10)_SDA1)
P4_POWA: IC2.18 (OUTPUT_1), J29.A3
P4_POWA_C: IC2.1 (INPUT_1), U3.3 (W3)
P4_POWB: IC2.17 (OUTPUT_2), J29.A7
P4_POWB_C: IC2.2 (INPUT_2), U3.5 (W5(FS_N))
P5_DIO_A: J29.A9, U3.43 (W43(Y11))
P5_DIO_B: J29.A12, U3.56 (W56)
P5_POWA: IC2.15 (OUTPUT_4), J29.A11
P5_POWA_C: IC2.4 (INPUT_4), U3.32 (W32)
P5_POWB: IC2.16 (OUTPUT_3), J29.A15
P5_POWB_C: IC2.3 (INPUT_3), U3.9 (W9(FS_P))
P6_DIO_A: J29.A17, U3.16 (W16)
P6_DIO_B: J29.A20, U3.22 (W22)
P6_POWA: IC2.12 (OUTPUT_7), J29.A19
P6_POWA_C: IC2.7 (INPUT_7), U3.23 (W23)
P6_POWB: IC2.13 (OUTPUT_6), J29.A23
P6_POWB_C: IC2.6 (INPUT_6), U3.34 (W34)
PDO2: IC4.20 (POWER_OK2)
PDO3: IC4.14 (POWER_OK3)
RFID_RX: J31/32.2 (RX), U3.52 (W52(Y2)_RX1)
RFID_TX: J31/32.3 (TX), U3.54 (W54(Y1)_TX1)
RX1+: J1.B11
RX1-: J1.B10
RX2+: J1.A11
RX2-: J1.A10
SBU1: J1.A8
SBU2: J1.B8
SPI_CLK: J3.3, U3.49 (W49(Y6))
SPI_MISO: J3.2, U3.53 (W53(Y7))
SPI_MOSI: J3.1, U3.57 (W57(Y8))
SPI_SS: J3.4, U3.45 (W45(Y5))
TX1+: J1.A2
TX1-: J1.A3
TX2+: J1.B2
TX2-: J1.B3
U_SCL: IC4.7 (SCL), J2.4, R12.1
U_SDA: IC4.8 (SDA), J2.3, R11.1
VBUS: C2.1, D6.2, IC4.24 (VDD_), J1.A4, J1.A9, J1.B4, J1.B9, Q1.1 (S_1), Q1.2 (S_2), Q1.3 (S_3), R7.1, R18.2
VC: J30.2, J31/32.11 (VC)
VDD: D2.1, IC4.22 (VSYS), J2.2, R11.2, R12.2, R14.2, R15.2, S3.2 (in2)
VR: J30.3, J31/32.12 (VR)
VS: C1.2, C5.1, C7.1, D3.2, J24.1, Q1.5 (D), R8.2, U1.1 (IN), U2.1 (+VIN)

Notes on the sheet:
IP67 panel-mount USB C Connector
The RFID multiplex is configured by default using channels I1_CON_C (W46), I2_CON_C (W73) and I3_CON_C (W25). Switching the jumpers allows 12V switching as an alternative function via I1_POW_C, I2_POW_C and I3_POWC.
8V to 28V compatible
Alternate Power Supply 15-27V
J2 allows progreamming of the STUSB4500QTR to set USB-PD parameters
User Jumpers (RFID)
DAC1 is available via internal header or via P3_DIO_C. DAC2 is available via internal header or via P4_DIO_C. BNC1 is mirrored on P5_DIO_C. BNC2 is mirrored on P6_DIO_C.
3x Toshiba TBD62084AFWG provide switching for up to 23 x 12V inductive loads.
15V to 27V compatible
USB-C Power Delivery Must leave unpopulated if using alternative power supply connector
Do not populate USB PD circuit if this is in use
I2C: I2C1 is available on port 4 via P4_DIO_A (SCL; W59) and P4_DIO_B (SDA; W55). I2C2 is available on the internal I2C header via I2C_SDA (W8) and I2C_SCL (W12). UART: UART1 is available via the RFID board header on RFID_TX (W54) and RFID_RX (W52). UART2 is available on port 1 via: P1_DIO_A (TX; W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
User Jumpers (I2C)
Reset button
Switch for user input
Microprocessor Connector (Pyboard D) 80 pin connection via 2x Hirose connectors on base
voltage regulation
Diode provides voltage drop for PyBoard D
Ethernet Connector (unpopulated)
Power breakouts for peripherals (unswitched)
Internal ports for nosepokes (I1-3)
The default behaviour for P3_DIO_A and P3_DIO_B is to replicate I2_DIO_A (W24) and I2_DIO_B (W51). Switching the jumpers allows for the I2C_SCL (W12) and I2C_SDA (W8) to be broken out on these lines instead. This allows access to the I2C interface (e.g. for port expanders) via ethernet Port 3 in li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
Inputs/Outputs
Internal Solenoids/12V lines (via TBD62084AFWG)
RFID circuits (unpopulated)
These connections are intended for UART connection of the RFIDRW-E-TTL board from Priority 1. The G3VM Mosfet relay can be used for switching between up to 3 RFID antennae with a single board. If using a single coil the Mult_Disable jumper can be used with a single antenna connected. https://www.pr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
Solenoid Drivers
0-3.3V UART

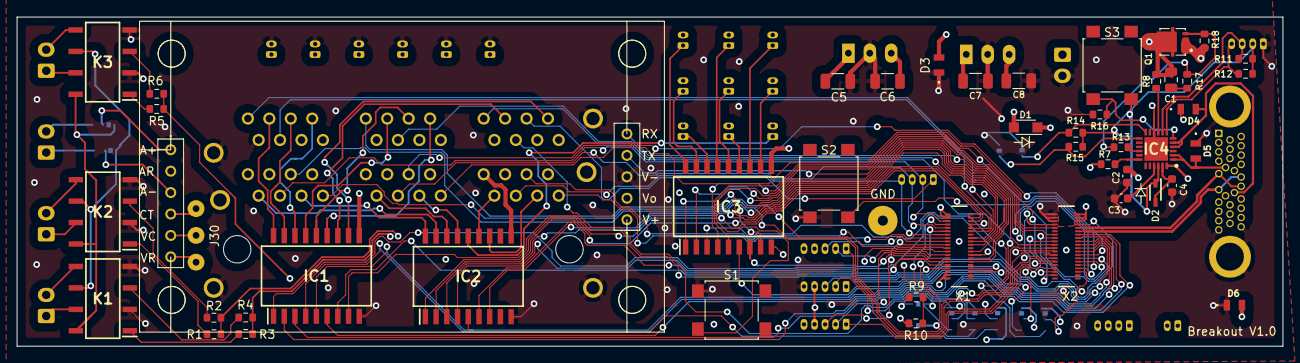
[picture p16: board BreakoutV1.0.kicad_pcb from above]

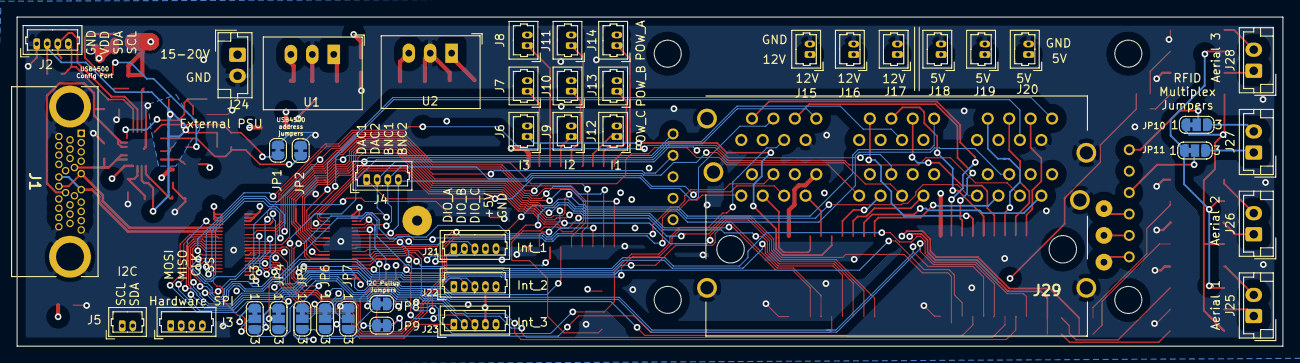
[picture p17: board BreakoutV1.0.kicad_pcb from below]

Board: 4 copper layers, 150.0 x 39.0 mm, 91 parts (42 on the bottom side), 134 nets.

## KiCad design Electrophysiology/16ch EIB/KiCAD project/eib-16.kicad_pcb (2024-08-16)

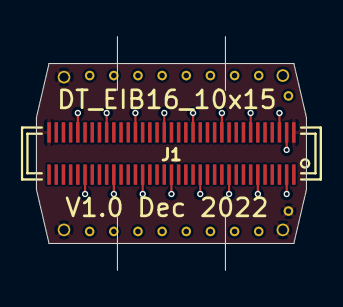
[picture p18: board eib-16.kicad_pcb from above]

Board: 4 copper layers, 15.0 x 10.0 mm, 21 parts (0 on the bottom side), 17 nets.

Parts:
GND0: LRG_GP; GOLDPIN_0.5ID_0.7OD
GND1: LFP; GOLDPIN_0.5ID_0.7OD
J1: DF40-REC; DF40-70REC
LFP1, LFP2, LFP3, LFP4, LFP5, LFP6, LFP7, LFP8, LFP9, LFP10, LFP11, LFP12, LFP13, LFP14, LFP15: 1; LFP_Port
LFP16: 0; LFP_Port
REF1: LFP; GOLDPIN_0.5ID_0.7OD
SHLD_A1: LRG_GP; GOLDPIN_0.5ID_0.7OD

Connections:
GND: GND0.P$1 (0), GND1.P$1 (0), J1.36, J1.70, SHLD_A1.P$1 (0)
unnamed: J1.2, LFP1.0
unnamed: J1.6, LFP2.0
unnamed: J1.10, LFP3.0
unnamed: J1.14, LFP4.0
unnamed: J1.18, LFP5.0
unnamed: J1.22, LFP6.0
unnamed: J1.26, LFP7.0
unnamed: J1.30, LFP8.0
unnamed: J1.40, LFP16.0
unnamed: J1.44, LFP15.0
unnamed: J1.48, LFP14.0
unnamed: J1.52, LFP13.0
unnamed: J1.56, LFP12.0
unnamed: J1.60, LFP11.0
unnamed: J1.64, LFP10.0
unnamed: J1.68, LFP9.0

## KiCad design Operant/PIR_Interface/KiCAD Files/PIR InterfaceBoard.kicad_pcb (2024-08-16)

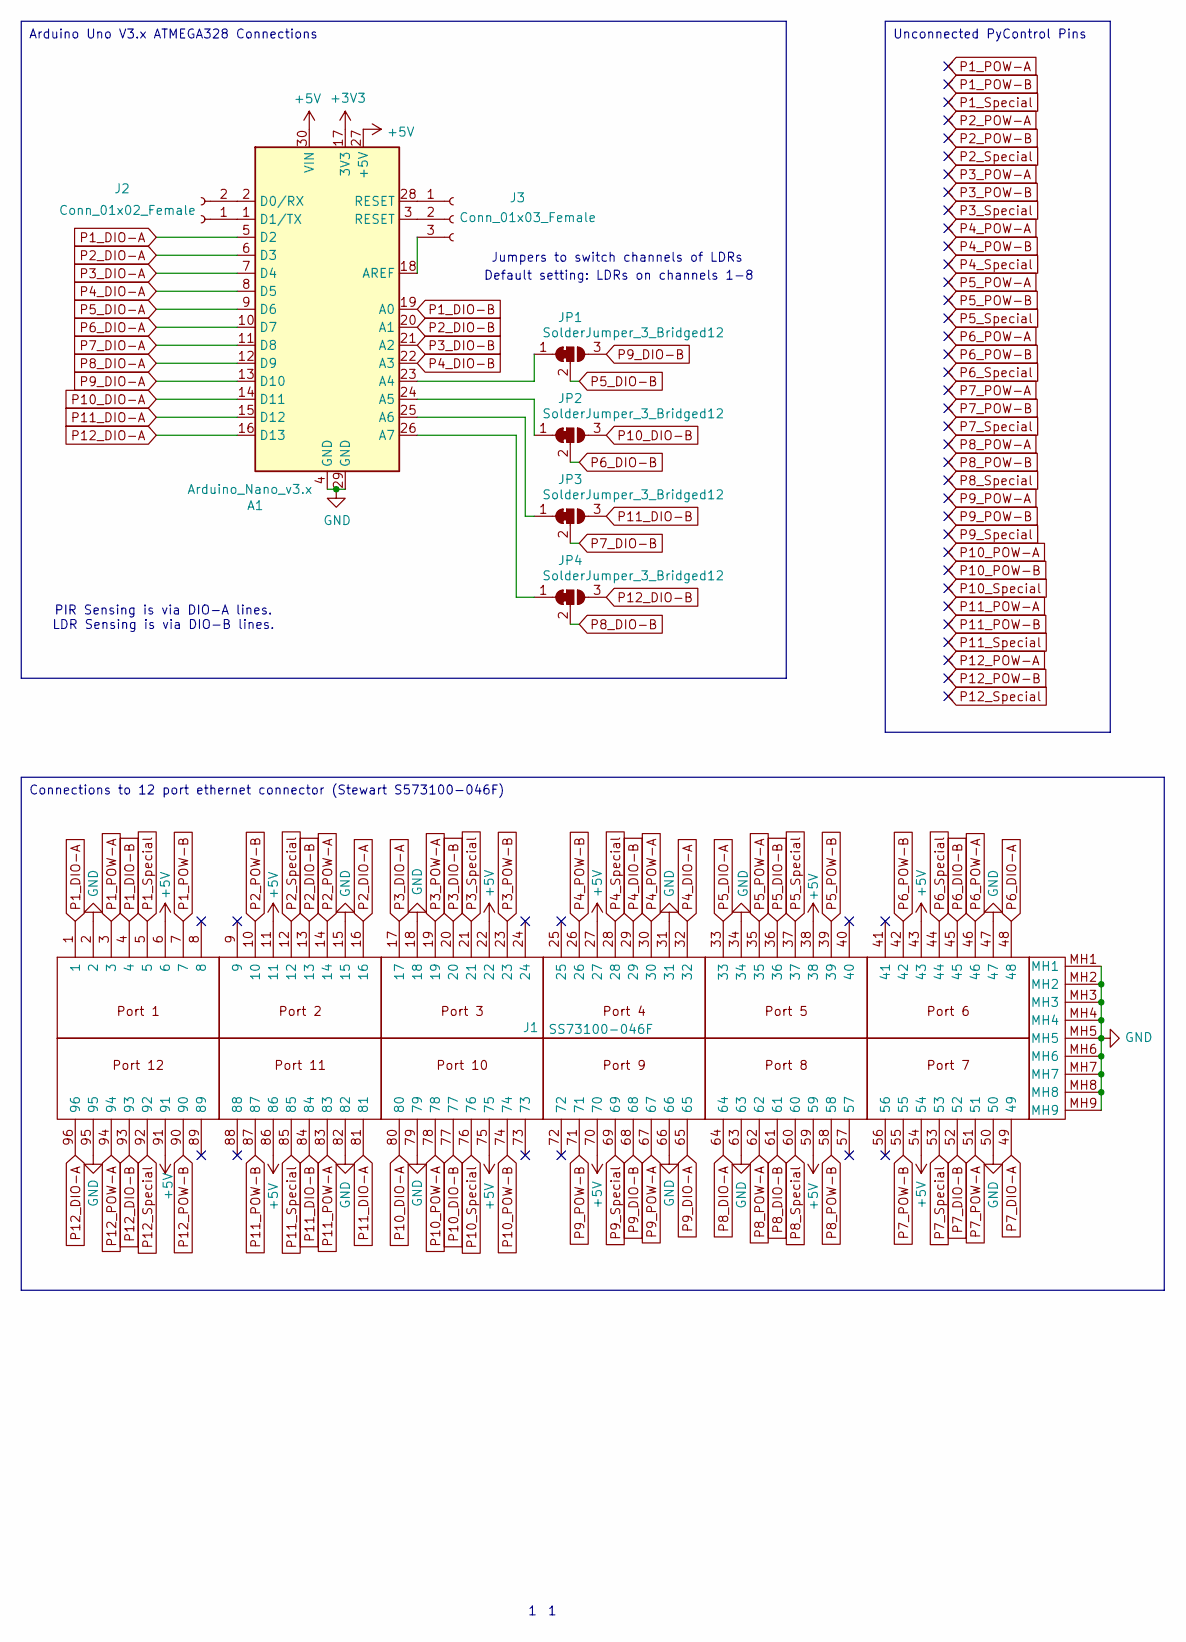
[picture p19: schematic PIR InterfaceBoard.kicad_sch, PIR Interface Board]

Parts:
A1: Arduino_Nano_v3.x; Arduino_Nano
J1: SS73100-046F; SS73100046F; Mouser Part Number 530-SS73100-046F
J2: Conn_01x02_Female; PinHeader_1x02_P2.54mm_Vertical
J3: Conn_01x03_Female; PinHeader_1x03_P2.54mm_Vertical
JP1, JP2, JP3, JP4: SolderJumper_3_Bridged12; SolderJumper-3_P1.3mm_Bridged12_RoundedPad1.0x1.5mm_NumberL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

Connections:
+3V3: A1.17 (3V3)
+5V: A1.27 (+5V), A1.30 (VIN), J1.6, J1.11, J1.22, J1.27, J1.38, J1.43, J1.54, J1.59, J1.70, J1.75, J1.86, J1.91
GND: A1.4 (GND), A1.29 (GND), J1.2, J1.15, J1.18, J1.31, J1.34, J1.47, J1.50, J1.63, J1.66, J1.79, J1.82, J1.95, J1.MH1, J1.MH2, J1.MH3, J1.MH4, J1.MH5, J1.MH6, J1.MH7, J1.MH8, J1.MH9
unnamed: A1.1 (D1/TX), J2.1
unnamed: A1.2 (D0/RX), J2.2
unnamed: A1.3 (RESET), J3.2
unnamed: A1.18 (AREF), J3.3
unnamed: A1.23 (A4), JP1.1 (A)
unnamed: A1.24 (A5), JP2.1 (A)
unnamed: A1.25 (A6), JP3.1 (A)
unnamed: A1.26 (A7), JP4.1 (A)
unnamed: A1.28 (RESET), J3.1
P1_DIO-A: A1.5 (D2), J1.1
P1_DIO-B: A1.19 (A0), J1.4
P1_POW-A: J1.3
P1_POW-B: J1.7
P1_Special: J1.5
P2_DIO-A: A1.6 (D3), J1.16
P2_DIO-B: A1.20 (A1), J1.13
P2_POW-A: J1.14
P2_POW-B: J1.10
P2_Special: J1.12
P3_DIO-A: A1.7 (D4), J1.17
P3_DIO-B: A1.21 (A2), J1.20
P3_POW-A: J1.19
P3_POW-B: J1.23
P3_Special: J1.21
P4_DIO-A: A1.8 (D5), J1.32
P4_DIO-B: A1.22 (A3), J1.29
P4_POW-A: J1.30
P4_POW-B: J1.26
P4_Special: J1.28
P5_DIO-A: A1.9 (D6), J1.33
P5_DIO-B: J1.36, JP1.2 (C)
P5_POW-A: J1.35
P5_POW-B: J1.39
P5_Special: J1.37
P6_DIO-A: A1.10 (D7), J1.48
P6_DIO-B: J1.45, JP2.2 (C)
P6_POW-A: J1.46
P6_POW-B: J1.42
P6_Special: J1.44
P7_DIO-A: A1.11 (D8), J1.49
P7_DIO-B: J1.52, JP3.2 (C)
P7_POW-A: J1.51
P7_POW-B: J1.55
P7_Special: J1.53
P8_DIO-A: A1.12 (D9), J1.64
P8_DIO-B: J1.61, JP4.2 (C)
P8_POW-A: J1.62
P8_POW-B: J1.58
P8_Special: J1.60
P9_DIO-A: A1.13 (D10), J1.65
P9_DIO-B: J1.68, JP1.3 (B)
P9_POW-A: J1.67
P9_POW-B: J1.71
P9_Special: J1.69
P10_DIO-A: A1.14 (D11), J1.80
P10_DIO-B: J1.77, JP2.3 (B)
P10_POW-A: J1.78
P10_POW-B: J1.74
P10_Special: J1.76
P11_DIO-A: A1.15 (D12), J1.81
P11_DIO-B: J1.84, JP3.3 (B)
P11_POW-A: J1.83
P11_POW-B: J1.87
P11_Special: J1.85
P12_DIO-A: A1.16 (D13), J1.96
P12_DIO-B: J1.93, JP4.3 (B)
P12_POW-A: J1.94
P12_POW-B: J1.90
P12_Special: J1.92

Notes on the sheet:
Arduino Uno V3.x ATMEGA328 Connections
Connections to 12 port ethernet connector (Stewart S573100-046F)
Unconnected PyControl Pins
Default setting: LDRs on channels 1-8
Jumpers to switch channels of LDRs
PIR Sensing is via DIO-A lines. LDR Sensing is via DIO-B lines.

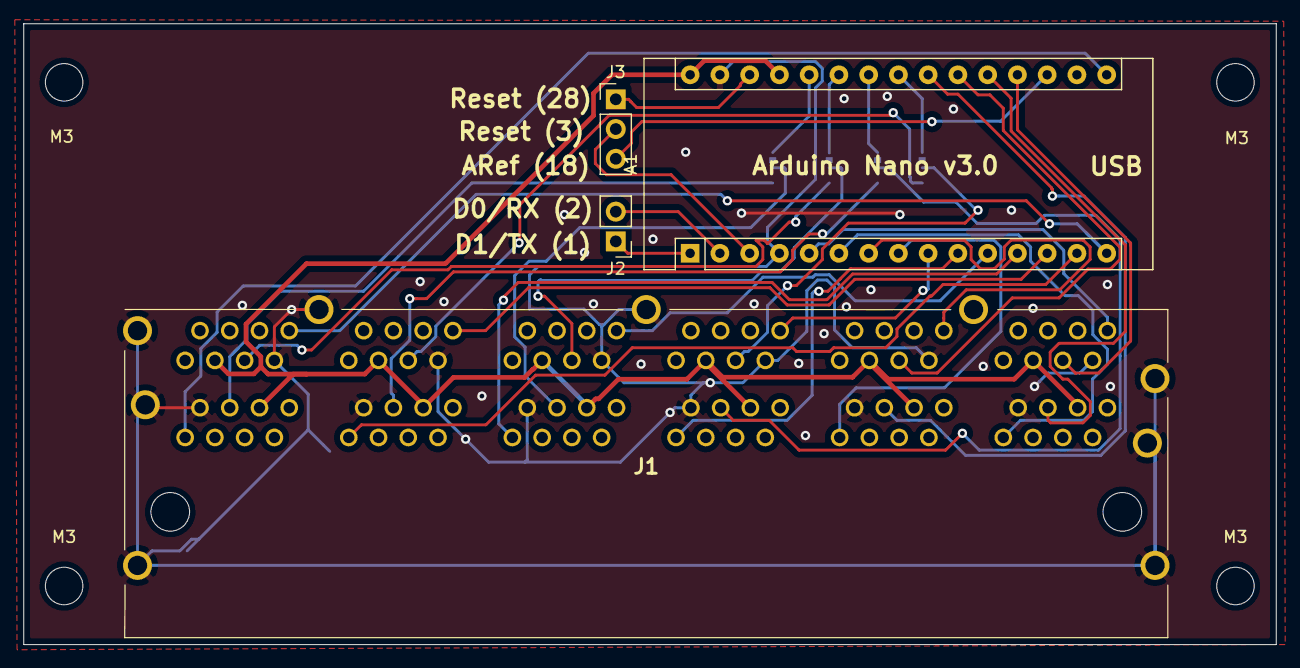
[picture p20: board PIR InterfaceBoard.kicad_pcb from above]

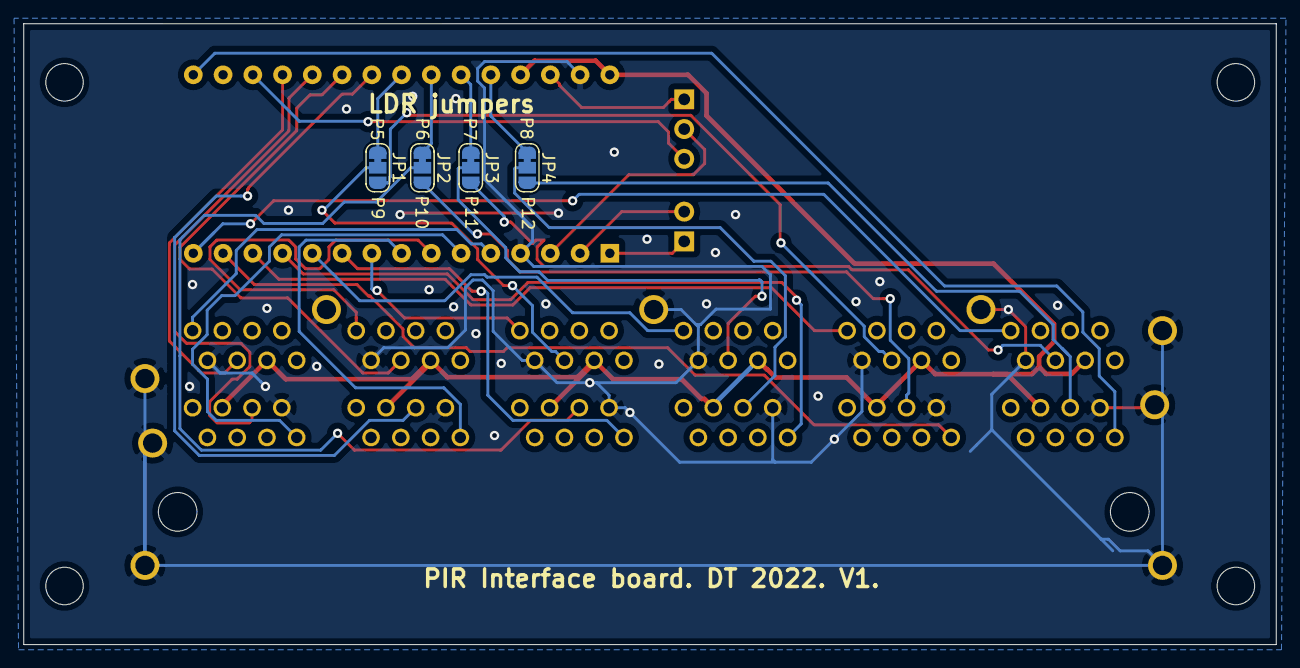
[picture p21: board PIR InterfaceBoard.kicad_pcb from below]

Board: 2 copper layers, 106.9 x 53.0 mm, 12 parts (4 on the bottom side), 35 nets.

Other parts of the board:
M3, M3#2, M3#3, M3#4: MountingHole_3.2mm_M3

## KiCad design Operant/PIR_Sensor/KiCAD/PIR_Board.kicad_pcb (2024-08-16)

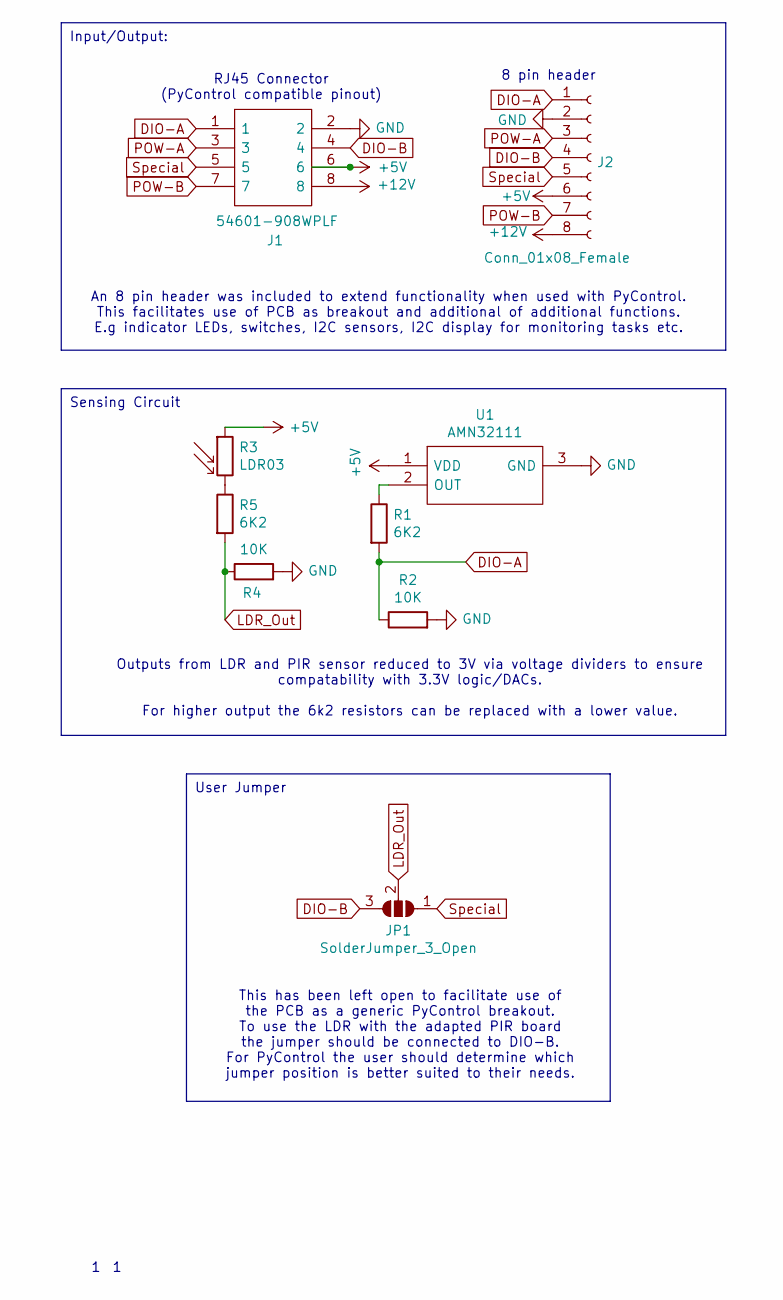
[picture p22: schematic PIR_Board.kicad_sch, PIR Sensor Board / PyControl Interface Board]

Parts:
J1: 54601-908WPLF; 54601908WPLF; Mouser Part Number 649-54601-908WPLF
J2: Conn_01x08_Female; PinSocket_1x08_P2.54mm_Vertical
JP1: SolderJumper_3_Open; SolderJumper-3_P1.3mm_Open_RoundedPad1.0x1.5mm_NumberLabels
R1, R5: 6K2; R_1206_3216Metric_Pad1.42x1.75mm_HandSolder
R2, R4: 10K; R_1206_3216Metric_Pad1.42x1.75mm_HandSolder
R3: LDR03; PinSocket_1x02_P2.54mm_Vertical
U1: AMN32111; AMN33111; Mouser Part Number 769-AMN32111

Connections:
+5V: J1.6, J2.6, R3.1, U1.1 (VDD)
+12V: J1.8, J2.8
DIO-A: J1.1, J2.1, R1.2, R2.1
DIO-B: J1.4, J2.4, JP1.3 (B)
GND: J1.2, J2.2, R2.2, R4.2, U1.3 (GND)
LDR_Out: JP1.2 (C), R4.1, R5.2
unnamed: R1.1, U1.2 (OUT)
unnamed: R3.2, R5.1
POW-A: J1.3, J2.3
POW-B: J1.7, J2.7
Special: J1.5, J2.5, JP1.1 (A)

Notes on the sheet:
Sensing Circuit
Input/Output:
User Jumper
An 8 pin header was included to extend functionality when used with PyControl. This facilitates use of PCB as breakout and additional of additional functions. E.g indicator LEDs, switches, I2C sensors, I2C display for monitoring tasks etc.
Outputs from LDR and PIR sensor reduced to 3V via voltage dividers to ensure compatability with 3.3V logic/DACs. For higher output the 6k2 resistors can be replaced with a lower value.
This has been left open to facilitate use of the PCB as a generic PyControl breakout. To use the LDR with the adapted PIR board the jumper should be connected to DIO-B. For PyControl the user should determine which jumper position is better suited to their needs.
RJ45 Connector (PyControl compatible pinout)
8 pin header

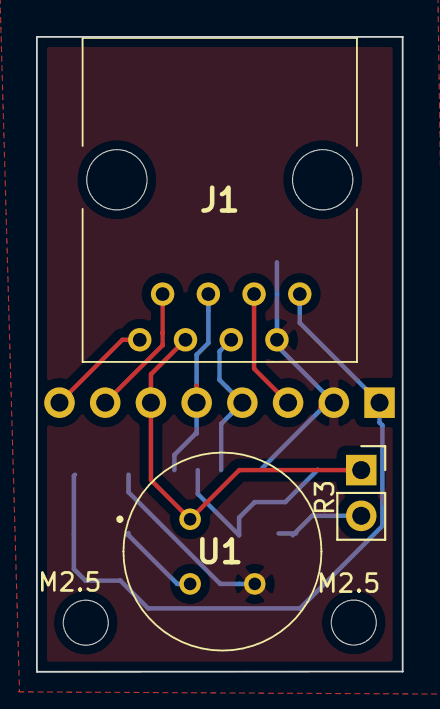
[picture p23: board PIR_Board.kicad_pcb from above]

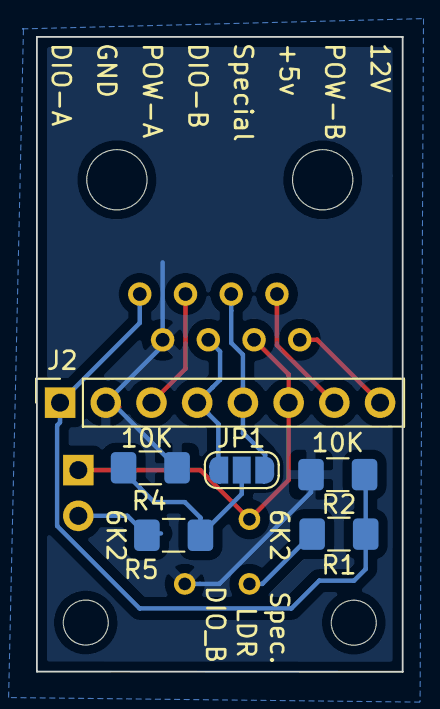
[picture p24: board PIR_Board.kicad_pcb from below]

Board: 2 copper layers, 20.3 x 35.3 mm, 11 parts (6 on the bottom side), 11 nets.

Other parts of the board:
M2.5, M2.5#2: MountingHole_2.5mm

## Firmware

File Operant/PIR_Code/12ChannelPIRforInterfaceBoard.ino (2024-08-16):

//This sketch was adapted from the 6 channel code in the COMPASS paper.
//Data is sent every second across a serial (USB) connection, as a comma-separated string of values.
// The sketch is written longhand, in an attempt to improve clarity.  Use of arrays for values and counters to improve brevity and flexibility:
// http://arduino.cc/en/Reference/For  for details on arrays  and
// http://arduino.cc/en/Reference/While  for other timing options


// Please refer to schematic and solder jumpers to identify which channel Light dependent resistors (LDRs) are reading from

String ID = "D";  // data header
int LDRPin1 = A0;     //pin definition for LDR1
int LDRPin2 = A1;     //pin definition for LDR2
int LDRPin3 = A2;     //pin definition for LDR3
int LDRPin4 = A3;     //pin definition for LDR4
int LDRPin5 = A4;     //pin definition for LDR5
int LDRPin6 = A5;     //pin definition for LDR6
int LDRPin7 = A6;     //pin definition for LDR7
int LDRPin8 = A7;     //pin definition for LDR8

int PIR1 = 2;     //pin definition for PIR1
int PIR2 = 3;     //pin definition for PIR2
int PIR3 = 4;     //pin definition for PIR3
int PIR4 = 5;     //pin definition for PIR4
int PIR5 = 6;     //pin definition for PIR5
int PIR6 = 7;     //pin definition for PIR6
int PIR7 = 8;     //pin definition for PIR7
int PIR8 = 9;     //pin definition for PIR8
int PIR9 = 10;    //pin definition for PIR9
int PIR10 = 11;   //pin definition for PIR10
int PIR11 = 12;   //pin definition for PIR11
int PIR12 = 13;   //pin definition for PIR12

int PIRCounter1 = 0;   //activity counter for PIR1
int PIRCounter2 = 0;   //activity counter for PIR2
int PIRCounter3 = 0;   //activity counter for PIR3
int PIRCounter4 = 0;   //activity counter for PIR4
int PIRCounter5 = 0;   //activity counter for PIR5
int PIRCounter6 = 0;   //activity counter for PIR6
int PIRCounter7 = 0;   //activity counter for PIR7
int PIRCounter8 = 0;   //activity counter for PIR8
int PIRCounter9 = 0;   //activity counter for PIR9
int PIRCounter10 = 0;  //activity counter for PIR10
int PIRCounter11 = 0;  //activity counter for PIR11
int PIRCounter12 = 0;  //activity counter for PIR12

int LoopCounter = 0; //loopcounter for activity

void setup() {

  Serial.begin(57600);
  // give time for startup
  delay(5000);
}

// This section runs in a loop constantly
// sensors are polled every 100msec
// data sent via serial every second
void loop() {

  // read all the input pins:
  int PIRState1 = digitalRead(PIR1);
  int PIRState2 = digitalRead(PIR2);
  int PIRState3 = digitalRead(PIR3);
  int PIRState4 = digitalRead(PIR4);
  int PIRState5 = digitalRead(PIR5);
  int PIRState6 = digitalRead(PIR6);
  int PIRState7 = digitalRead(PIR7);
  int PIRState8 = digitalRead(PIR8);
  int PIRState9 = digitalRead(PIR9);
  int PIRState10 = digitalRead(PIR10);
  int PIRState11 = digitalRead(PIR11);
  int PIRState12 = digitalRead(PIR12);

  if (LoopCounter < 10) { 
    // measurements will keep looping until 1 sec is up (10 x 100 msec)
    // if the state is high, increment the relevent PIRcounter
    if (PIRState1 == HIGH) {
      // e.g. if the current state of PIR1 is HIGH then add 1 to the PIR1 counter:
      PIRCounter1++;
    }
    if (PIRState2 == HIGH) {
      PIRCounter2++;
    }
    if (PIRState3 == HIGH) {
      PIRCounter3++;
    }
    if (PIRState4 == HIGH) {
      PIRCounter4++;
    }
    if (PIRState5 == HIGH) {
      PIRCounter5++;
    }
    if (PIRState6 == HIGH) {
      PIRCounter6++;
    }
    if (PIRState7 == HIGH) {
      PIRCounter7++;
    }
    if (PIRState8 == HIGH) {
      PIRCounter8++;
    }
    if (PIRState9 == HIGH) {
      PIRCounter9++;
    }
    if (PIRState10 == HIGH) {
      PIRCounter10++;
    }
    if (PIRState11 == HIGH) {
      PIRCounter11++;
    }
    if (PIRState12 == HIGH) {
      PIRCounter12++;
    }
    delay(100);  // wait 100msec before polling inputs again.  
    //This timing can be varied to ensure consistent 1 sec updates.
    LoopCounter++;
  }
  else {

    //send HEADER indicating data follows
    Serial.print(ID);
    // separate with a comma
    Serial.print(",PIRs:,");
    // send total activity for PIR counters, separated by commas
    Serial.print(PIRCounter1);
    Serial.print(",");
    Serial.print(PIRCounter2);
    Serial.print(",");
    Serial.print(PIRCounter3);
    Serial.print(",");
    Serial.print(PIRCounter4);
    Serial.print(",");
    Serial.print(PIRCounter5);
    Serial.print(",");
    Serial.print(PIRCounter6);
    Serial.print(",");
    Serial.print(PIRCounter7);
    Serial.print(",");
    Serial.print(PIRCounter8);
    Serial.print(",");
    Serial.print(PIRCounter9);
    Serial.print(",");
    Serial.print(PIRCounter10);
    Serial.print(",");
    Serial.print(PIRCounter11);
    Serial.print(",");
    Serial.print(PIRCounter12);
    Serial.print(",LDRs:,");
    // read LDRs connected to relevant pins and send resulting number
    Serial.print(analogRead(LDRPin1));
    Serial.print(",");
    Serial.print(analogRead(LDRPin2));
    Serial.print(",");
    Serial.print(analogRead(LDRPin3));
    Serial.print(",");
    Serial.print(analogRead(LDRPin4));
    Serial.print(",");
    Serial.print(analogRead(LDRPin5));
    Serial.print(",");
    Serial.print(analogRead(LDRPin6));
    Serial.print(",");
    Serial.print(analogRead(LDRPin7));
    Serial.print(",");
    Serial.print(analogRead(LDRPin8));
    Serial.print(",");
    Serial.print('\n'); // new line (linefeed) character
    LoopCounter = 0; // reset your loops
    PIRCounter1 = 0; // and your individual counters
    PIRCounter2 = 0;
    PIRCounter3 = 0;
    PIRCounter4 = 0;
    PIRCounter5 = 0;
    PIRCounter6 = 0;
    PIRCounter7 = 0;
    PIRCounter8 = 0;
    PIRCounter9 = 0;
    PIRCounter10 = 0;
    PIRCounter11 = 0;
    PIRCounter12 = 0;
  }
}

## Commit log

2024-08-16 Update Hardware Data
    [10X15M-B_Mask.gbr, 10X15M-B_Paste.gbr, 10X15M-B_SilkS.gbr, 10X15M-Bottom.gbr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]
2024-08-17 CAD drawings added
    CAD drawings for operant unit added
    [BreakoutV1.0.kicad_pcb, Draft BOM.xlsx, FinalCageExtension.dwg, NosepokeV1.0.kicad_pcb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]

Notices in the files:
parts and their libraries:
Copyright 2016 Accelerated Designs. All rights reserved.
